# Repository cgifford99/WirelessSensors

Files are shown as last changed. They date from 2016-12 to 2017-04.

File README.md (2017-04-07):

# WirelessSensors
Wireless Sensors Flex Friday project repo

Here's a link to our Waffle.io management board: https://waffle.io/cgifford99/WirelessSensors/join

## Current Schedule
- [x] Project Proposal  | September 11th-September 30th
- [x] Research          | September 30th-October 7th
- [ ] Data pro design   | October 7th- December 23rd
- [ ] Testing/Debugging | December 23rd-April 7th 2017
- [ ] Finalize product  | March 3rd 2017-May 19th 2017
- [ ] Presentation      | May 19th 2017-June 9th 2017

# Wireless Sensors Proposal
## Abstract
The Wireless Sensor group’s overall goal is to create an easier and more cost-effective way to wirelessly transmit data from classroom   experiments from sensors through a communication chip to internet-enabled devices such as computers, laptops, tablets and smartphones. This system will allow students to easily customize how data is collected and manipulate data to fit their needs. It also allows teachers to view   the student’s data. Although this system will be useful in many fields, the project is going to initially focus on the educational market. This technology currently exists from other corporations, but it’s slow, expensive, complicated and unreliable. The team’s alternative will be faster, less expensive, user friendly and will deliver consistent results again and again. Furthermore, the current systems use wires, that get tangled and get lost. All of these wires can be eliminated with the use of radio communication and this is what the Wireless Sensor Team plans to do.

## Problem Statement
Currently there is no easy way to collect, store and share data from classroom science experiments simply by running the experiment and having data automatically appear on a shared website using low-cost components and inexpensive, yet effective software. Vernier is a company that produces a product along the lines of what we are creating, but it’s expensive, slow, and hard to access data. Products produced by Vernier, such as LabQuest, cost over $300 and need the use of another source, such as a PC, to process the collected data.

## Goals and Objectives
* Goal 1: Create a working prototype that sends information from a Raspberry Pi Zero/Arduino Micro to a Raspberry Pi 3.

  * Objective A: Discuss what teams are necessary, what project managing software to use, whether to use a Raspberry Pi Zero or an Arduino Micro to control the sensors and whether to make another prototype for the Rpi Zero or not.
  * Objective B: If the Rpi Zero is going to be used, code will need to be converted from the Arduino C++ language to C++ on the Rpi Zero.
  * Objective C: Create a prototype that includes the necessary components to interact with the Rpi 3 (the Hub).
  * Objective D: Debug data collection process and code (if necessary).

* Goal 2: Develop a cloud-based software for data storage and data transfer.

  * Objective A: Study Flask-SQLAlchemy (a framework to connect to a SQL database on the Rpi 3 and a browser on another device)
  * Objective B: Create and test a connection between the Rpi 3 SQL database and Flask-SQLAlchemy

* Goal 3: Finalize the product so that it both looks and works well for users.

  * Objective A: Design, order and solder a PCB (printed circuit board) that integrates with the Rpi Zero as well as the Rpi 3 in a more compact and visually attractive method.
  * Objective B: Use solidworks or another 3D design software to design an enclosure for the Rpi 3 and the Rpi Zero/Arduino Micro.
  * Objective C: Complete, debug and finish the product.
  
## Our Team
**Christopher Gifford**: Christopher is a Junior and project manager of the Wireless Sensors group. Last year he managed the sensors portion of the wireless group and learned a variety of other skills like 3D design, PCB design, and more C++ programming since then. 

**Lewis Woodard**: Lewis is a Sophomore at Baxter Academy for Technology and Science who is a part of the Wireless Sensors project for the second year. He hopes to focus his efforts in the project towards hardware and enclosures, which will include PCB design and using SolidWorks to design enclosures, cases, and other devices to contain sensors. Last year Lewis joined after completing the Pentathlon and worked on a combination of hardware, enclosures and software. Since last year, Lewis has gained more experience in C++ programming, CAD and more. Lewis plans to use this knowledge to focus mainly on hardware, pcb and 3D design, assisting on programming and software when he is needed.

**Connor Bell**: (NOTE: Connor is no longer involved with the project) Connor is a Junior at Baxter Academy for Technology and Science. He is a new addition to the Wireless Sensors project. He has taken multiple classes based around electronics and computer programming, and is currently learning as much as he can to have enough knowledge to be successful on this projects. Connor has programmed multiple web-based and non-web based programs in various languages such as Python and Javascript, both of which are relevant to the progress of this project.

**Curtis**: 
Curtis is a Sophomore at Baxter Academy for Technology and Science. He is also a new addition to the Wireless Sensors project. He has taken multiple classes based around electronics and computer programming. Curtis plans to concentrate on programming so that he be a productive member of the group.

**Ryan Cunningham**: Ryan is a freshman a Baxter. He is also a new addition to the Wireless Sensors project. He has lots of experience in HTML and CSS, he also is skilled in GUI design and graphics works. 

## Timeline
Currently unavailable

## Resources
* The school has tools like 3d printing software and equipment, soldering irons and other useful PCB design tools.
* Alan Lukas, Hal, Wells and Amory have backgrounds in programming, 3D design and PCB design and their knowledge will be very useful in the project.
* Currently an arduino prototype (Sensor prototype) and a Raspberry Pi 3 prototype (Hub prototype), are functioning from last year.    However, the Arduino did not have sufficient memory to hold a large number of different data acquisition formats.    The current plan is to use a RPi Zero instead for the Arduino for the sensor prototype.
* Purchase a  variety of Vernier sensors or borrow them as required from Baxter’s inventory.

## Constraints
* The team’s experience in PCB design, C++ programming, 3D design and other skill sets will influence how smoothly the project goes.
* There is not enough time this year to set-up a business and market the product to schools and other educational services.
* Accidents like damaging the circuits or short-circuiting them has been a problem in the past.
* There will be plenty of distractions and time constraints, but the team will use detailed schedules (Kanban and Gantter) to stay on track.

## Budget
Currently unavailable

## Deliverables
The final product will be a marketable platform to use in a classroom environment for experiments and laboratory tests in different subjects including physics, chemistry, and others. It will be made up of a Raspberry Pi Zeros (sensors) and a larger Raspberry Pi (hub). The hub will store and organize all data into a database and then send these data to a common cloud-based web server. Students can then connect to this web site to compare results of the data collected in the various class experiments. Note that data can also be collected from field experiments and then sent up to the cloud based server once the sensors connect to the RPi hub.

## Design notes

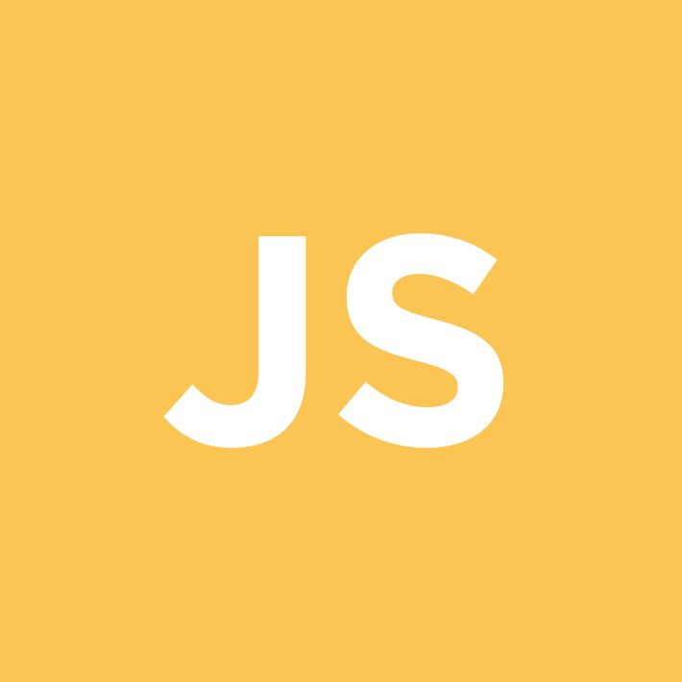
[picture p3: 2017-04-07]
server/client/images/user.jpg

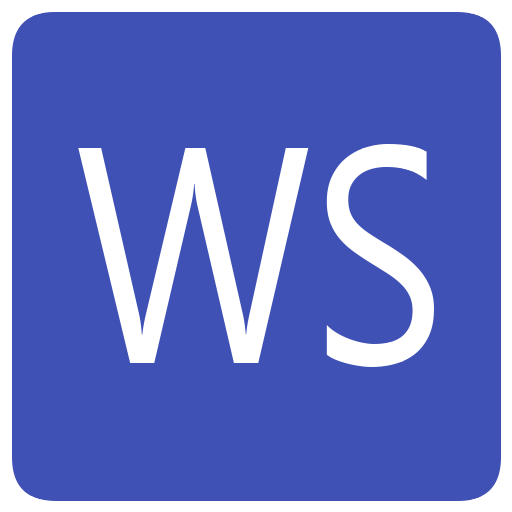
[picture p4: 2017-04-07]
server/client/images/android-desktop.png

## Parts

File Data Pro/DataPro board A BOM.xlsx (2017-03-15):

Part Name | Value | Device | Package | Description | Retailer | Retailer Part # | Manufacturer Part # | Quantity
B1 | CR2032 | CR2032SMT | CR2032-SMD |  | Digikey | BRX1-2032-SMCT-ND | BRX1-2032-SM | 1
C1 | 0.1uFd | C-USC0805 | C0805 | CAPACITOR, American symbol | Digikey | 311-1142-1-ND | CC0805KRX7R7BB104 | 2
D1 |  | DIODESOD-323F | SOD-323F | Diode | Digikey | MM3Z3V3BTR-ND | MM3Z3V3B | 1
D3 |  | DIODESMB | SMB-DIODE | Diode | Digikey | 1SMB5928BT3GOSCT-ND | 1SMB5928BT3G | 1
IC1 | 4049N | 4049N | DIL16 | Hex inverting BUFFER | Digikey | 296-29273-1-ND | CD74HC4049NSR | 1
IC2 | MCP3008 | MCP3008 | DIL16 |  | Digikey | MCP3008-I/P-ND | MCP3008-I/P | 1
IC3, IC7 | LM324D | LM324D | SO14 | OP AMP | Digikey | 497-1580-1-ND | LM324DT | 2
J1 | RASPBERRYPI-40-PIN-GPIO | RASPBERRYPI-40-PIN-GPIO | 2X20-SHROUDED | Raspberry Pi GPIO Header | Digikey | 1528-1785-ND | 2222 | 1
J2-J5 | A2 | M06VERNIER-ANALOG | BTA | Header 6 | https://www.sparkfun.com/products/12753 |  |  | 4
J6-J9 | D1 | M06VERNIER-DIGITAL | BTD | Header 6 | https://www.sparkfun.com/products/12754 |  |  | 4
JP2 |  | PINHD-1X4 | 1X04 | PIN HEADER
JP3 |  | PINHD-1X2 | 1X02 | PIN HEADER
JP4 |  | PINHD-1X5 | 1X05 | PIN HEADER
LED1 |  | LEDCHIP-LED0805 | CHIP-LED0805 | LED | Digikey | 475-1278-1-ND | LS R976-NR-1 | 1
R1-R8, R10, R17-R26 | 1k | R-US_R0805 | R0805 | RESISTOR, American symbol | Digikey | 311-1.0KARCT-ND | RC0805JR-071KL | 17
R9 | 4.7k | R-US_R0805 | R0805 | RESISTOR, American symbol | Digikey | 311-4.70KCRCT-ND | RC0805FR-074K7L | 1
R11, R15, R16 | 3.3k | R-US_R0805 | R0805 | RESISTOR, American symbol | Digikey | 311-3.3KARCT-ND | RC0805JR-073K3L | 3
R12 | 200 | R-US_R0805 | R0805 | RESISTOR, American symbol | Digikey | 311-200CRTR-ND | RC0805FR-07200RL | 1
R13 | 1.5M | R-US_R0805 | R0805 | RESISTOR, American symbol | Digikey | 311-1.5MARTR-ND | RC0805JR-071M5L | 1
R14 | 510K | R-US_R0805 | R0805 | RESISTOR, American symbol | Digikey | 311-510KARCT-ND | RC0805JR-07510KL | 1
U$2 | DS1307SO8-TIGHT | DS1307SO8-TIGHT | SO08-TIGHT | I2C real-time clock with battery backup. | Digikey | DS1307Z+T&RCT-ND | DS1307Z+T&R | 1
U1 | DS18B20 | DS18B20 | TO-92-AMMO | DS18B20 1-wire temperature sensor | Digikey | DS18B20+-ND | DS18B20+ | 1
X1 | 32.768khz | CRYSTALTC38H | TC38H | CRYSTAL | Digikey | 535-9034-ND | AB38T-32.768KHZ | 1

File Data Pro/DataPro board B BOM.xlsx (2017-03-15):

Part Name | Value | Device | Package | Description | Retailer | Retailer Part # | Manufacturer Part # | Quantity
BATT1 |  | JST_2PIN-SMT-RA | JST-PH-2-SMT-RA | JST 2-Pin Connectors of various flavors | Digikey | 455-1734-2-ND | B2B-PH-SM4-TB(LF)(SN) | 1
C1 | 2.2uF | C-USC0805 | C0805 | CAPACITOR, American symbol | Digikey | 587-1293-1-ND | EMK212BJ225KG-T | 1
C2 | 2.2uF | C-USC1206 | C1206 | CAPACITOR, American symbol | Digikey | 399-8180-1-ND | C1206C225K3RACTU | 1
C3 | 1uF | C-USC1206 | C1206 | CAPACITOR, American symbol | Digikey | 399-1254-1-ND | C1206C105K4RACTU | 1
C4 | 1uF | C-USC1206 | C1206 | CAPACITOR, American symbol | Digikey | 399-1254-1-ND | C1206C105K4RACTU | 1
C5 | 2.2uF | C-USC1206 | C1206 | CAPACITOR, American symbol | Digikey | 399-8180-1-ND | C1206C225K3RACTU | 1
C11 | 22uF | CAP0805 | C0805 | CAPACITOR, American symbol | Digikey | 490-10747-1-ND | GRM21BR61C226ME44L | 1
C12 | 0.1uF | CAP0603-CAP | 0603-CAP | CAPACITOR, American symbol | Digikey | 311-1088-1-ND | CC0603KRX7R7BB104 | 1
C13 | 0.1uF | CAP0603-CAP | 0603-CAP | CAPACITOR, American symbol | Digikey | 311-1088-1-ND | CC0603KRX7R7BB104 | 1
C14 | 10uF | CAP1206 | C1206 | CAPACITOR, American symbol | Digikey | 311-1376-1-ND | CC1206ZKY5V7BB106 | 1
C15 | 10uF | C-USC0805K | C0805K | CAPACITOR, American symbol | Digikey | 399-8012-1-ND | C0805C106K4PACTU | 1
C16 | 10uF | C-USC0805K | C0805K | CAPACITOR, American symbol | Digikey | 399-8012-1-ND | C0805C106K4PACTU | 1
C17 | 10uF | C-USC0805K | C0805K | CAPACITOR, American symbol | Digikey | 399-8012-1-ND | C0805C106K4PACTU | 1
C18 | 4700uF/10V | CPOL-USE5-13 | E5-13 | POLARIZED CAPACITOR, American symbol | Digikey | 493-1028-ND | UVR1A472MHD | 1
CHRG/LBO1 | ORANGE | LED0805_NOOUTLINE | CHIPLED_0805_NOOUTLINE | LED | Digikey | 160-1413-1-ND | LTST-C170KFKT | 1
CN2 | DCIN | DCBARRELSMT | DCJACK_2MM_SMT | DC Barrel Jack | Digikey | CP-002AHPJCT-ND | PJ-002AH-SMT-TR | 1
D1 | MBR0520LT | MBR0520LT | SOD123 | SCHOTTKY BARRIER RECTIFIER | Digikey | MBR0520LT1GOSTR-ND | MBR0520LT1G | 1
D2 | MBR0520LT | MBR0520LT | SOD123 | SCHOTTKY BARRIER RECTIFIER | Digikey | MBR0520LT1GOSTR-ND | MBR0520LT1G | 1
D3 | MBR0520LT | MBR0520LT | SOD123 | SCHOTTKY BARRIER RECTIFIER | Digikey | MBR0520LT1GOSTR-ND | MBR0520LT1G | 1
D4 | MBR120VLSFT1G | DIODESOD-123 | SOD-123 | Diode | Digikey | MBR120VLSFT1GOSTR-ND | MBR120VLSFT1G | 1
D5 | MBR0520LT | MBR0520LT | SOD123 | SCHOTTKY BARRIER RECTIFIER | Digikey | MBR0520LT1GOSTR-ND | MBR0520LT1G | 1
DONE1 | GREEN | LED0805_NOOUTLINE | CHIPLED_0805_NOOUTLINE | LED | Digikey | 475-1410-1-ND | LG R971-KN-1 | 1
IC8 | MCP73871 | MCP73871 | QFN20_4MM |  | Digikey | MCP73871-2AAI/ML-ND | MCP73871-2AAI/ML | 1
JP1 |  | PINHD-1X5 | 1X05 | PIN HEADER
JP2 | ESP8266 | PINHD-2X4 | 2X04 | PIN HEADER
JP3 |  | PINHD-1X4 | 1X04 | PIN HEADER
JP4 |  | PINHD-1X2 | 1X02 | PIN HEADER
L1 | 3.3uH | CR43 | CR43 | Power Inductor | Digikey | 308-1525-1-ND | CR43NP-3R3MC | 1
L2 | 4.7uH, 1.2A | INDUCTOR. | L3225M | Inductors | Digikey | 587-2166-1-ND | BRL3225T4R7M | 1
M1 | WIRELESS-NRF24L01 | WIRELESS-NRF24L01 | WIRELESS-NRF24L01 | 2.4 GHz Wireless Module based on NRF24L01 chip
PWR1 | RED | LED0805_NOOUTLINE | CHIPLED_0805_NOOUTLINE | LED | Digikey | 475-1415-2-ND | LH R974-LP-1 | 1
R1 | 13.3k | R-US_R0805 | R0805 | RESISTOR, American symbol | Digikey | 311-13.3KCRTR-ND | RC0805FR-0713K3L | 1
R2 | 147k | R-US_R0805 | R0805 | RESISTOR, American symbol | Digikey | 311-147KCRTR-ND | RC0805FR-07147KL | 1
R39 | 2M | RESISTOR0603-RES | 0603-RES | Resistor | Digikey | 311-2.0MGRTR-ND | RC0603JR-072ML | 1
R40 | 220k | RESISTOR0603-RES | 0603-RES | Resistor | Digikey | 311-220KJRTR-ND | RC0402JR-07220KL | 1
R41 | 1.2M | RESISTOR0603-RES | 0603-RES | Resistor | Digikey | 311-1.2MGRTR-ND | RC0603JR-071M2L | 1
R42 | 220k | RESISTOR0603-RES | 0603-RES | Resistor | Digikey | 311-220KJRTR-ND | RC0402JR-07220KL | 1
R43 | 2M | RESISTOR0603-RES | 0603-RES | Resistor | Digikey | 311-2.0MGRTR-ND | RC0603JR-072ML | 1
R44 | 270K | R-US_R0805 | R0805 | RESISTOR, American symbol | Digikey | 311-270KARTR-ND | RC0805JR-07270KL | 1
R45 | 100K | R-US_R0805 | R0805 | RESISTOR, American symbol | Digikey | 311-100KCRTR-ND | RC0805FR-07100KL | 1
R46 | 1K | R-US_R0805 | R0805 | RESISTOR, American symbol | Digikey | 311-1.0KARTR-ND | RC0805JR-071KL | 1
R47 | 1K | R-US_R0805 | R0805 | RESISTOR, American symbol | Digikey | 311-1.0KARTR-ND | RC0805JR-071KL | 1
R48 | 1K | R-US_R0805 | R0805 | RESISTOR, American symbol | Digikey | 311-1.0KARTR-ND | RC0805JR-071KL | 1
R49 | 2K | R-US_FLIPFLOP | 0805-THM | RESISTOR, American symbol |  |  |  | 1
R50 | 100K | R-US_R0805 | R0805 | RESISTOR, American symbol | Digikey | 311-100KCRTR-ND | RC0805FR-07100KL | 1
R51 | 1K | R-US_M0805 | M0805 | RESISTOR, American symbol | Digikey | 311-1.0KARTR-ND | RC0805JR-071KL | 1
RT1 | 150K | R-US_M0805 | M0805 | RESISTOR, American symbol | Digikey | 311-150KARTR-ND | RC0805JR-07150KL | 1
THERM1 | 10K | R-US_FLIPFLOP | 0805-THM | RESISTOR, American symbol
U$3 | V_REG_LD1117VXX | V_REG_LD1117VXX | 78XXL | LD1117VXX voltage regulator. We carry the 3.3V version (COM-00526) in TO-220 package. | Sparkfun | https://www.sparkfun.com/products/526 | https://www.sparkfun.com/products/526
U1 | LT1930AES5PBF | LT1930AES5PBF | SOT95P280X145-5N | DC/DC Converter | Digikey | LT1930AES5#TRMPBFTR-ND | LT1930AES5#TRMPBF | 1
U3 | TPS61200 | TPS61200 | QFN-10_PAD | DC to DC Booster | Digikey | 296-27017-1-ND | TPS61200DRCR | 1

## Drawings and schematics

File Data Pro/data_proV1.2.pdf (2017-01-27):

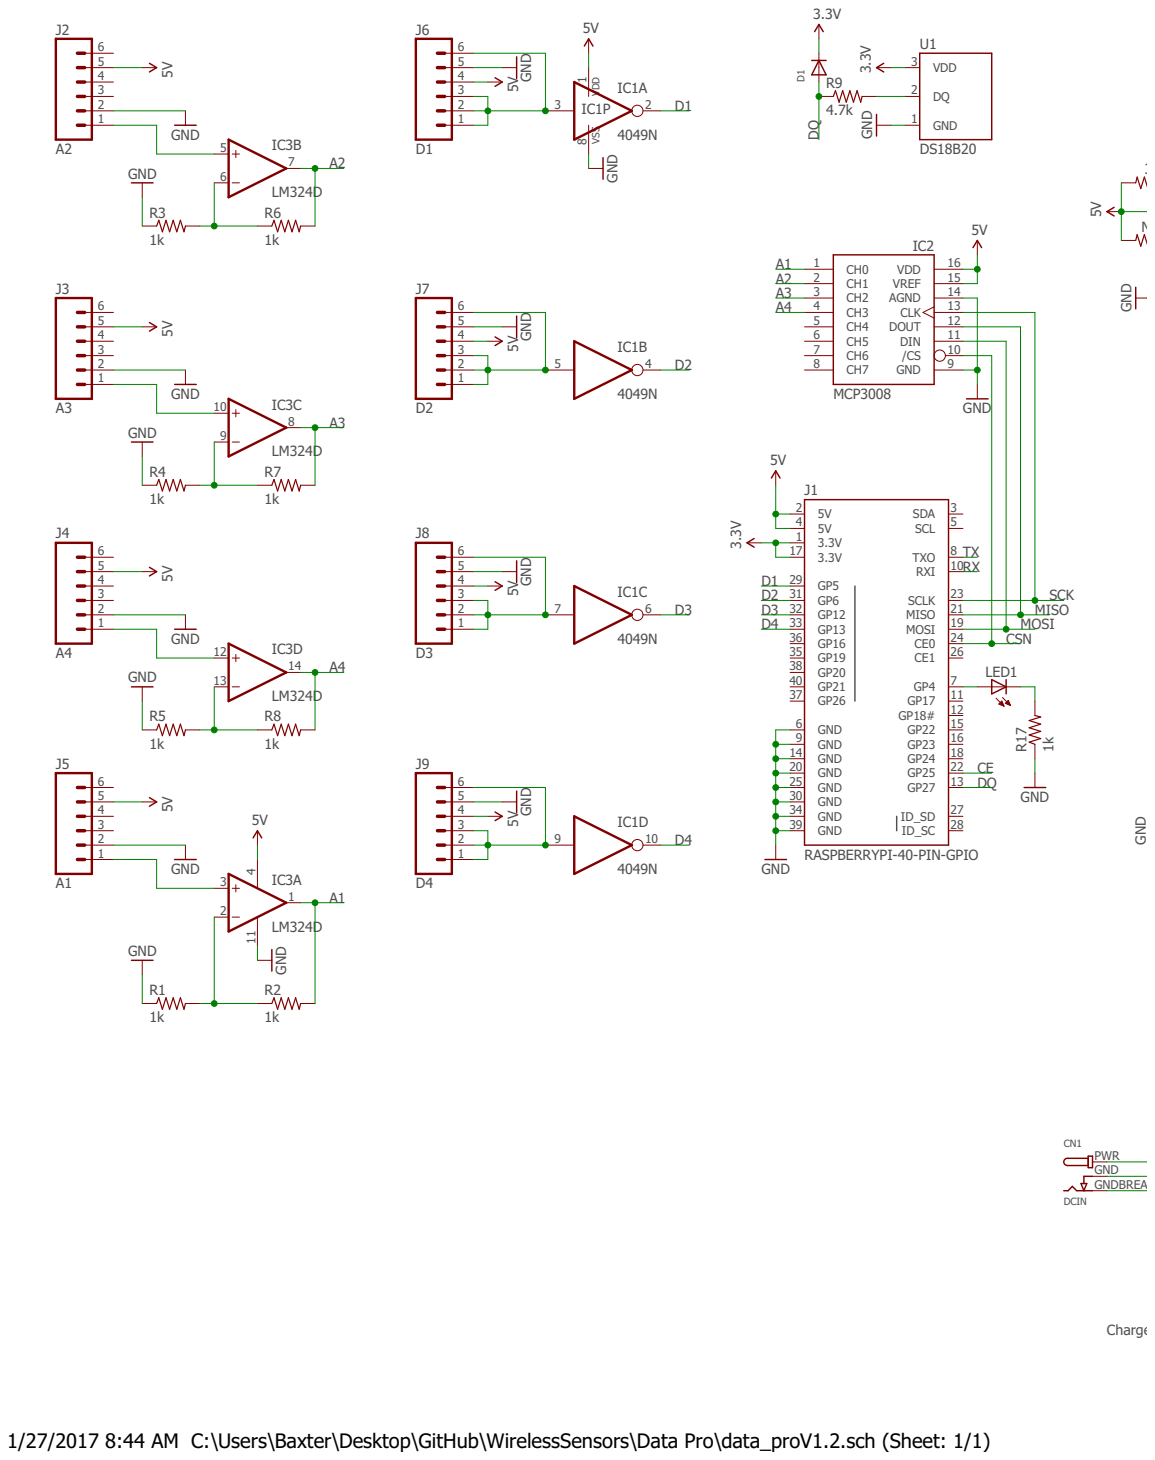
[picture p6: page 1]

1/27/2017 8:44 AM C:\Users\Baxter\Desktop\GitHub\WirelessSensors\Data Pro\data_proV1.2.sch (Sheet: 1/1)

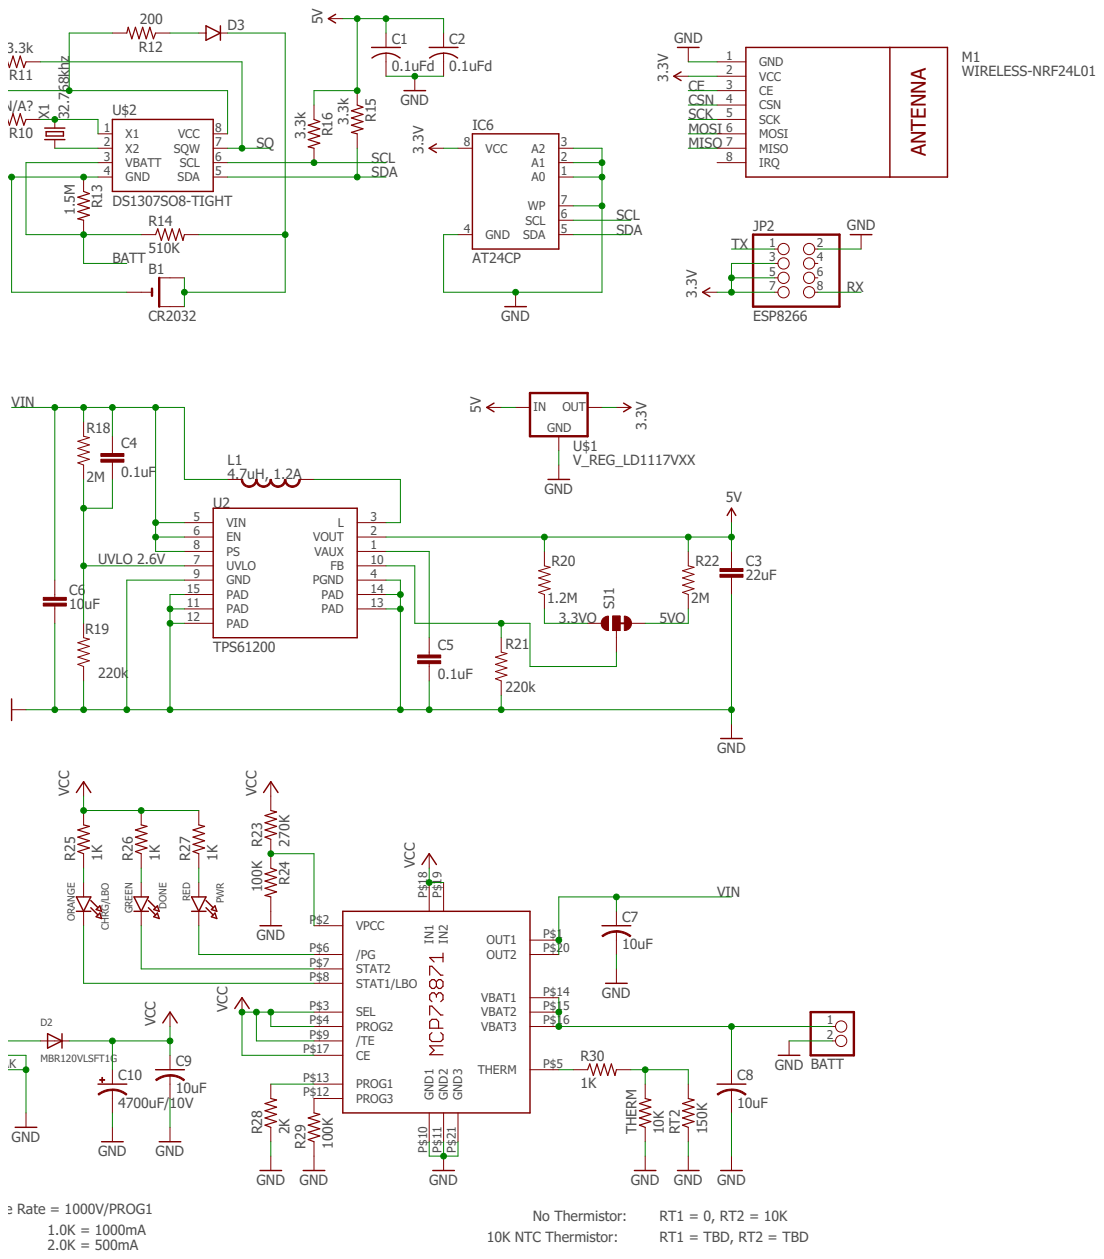
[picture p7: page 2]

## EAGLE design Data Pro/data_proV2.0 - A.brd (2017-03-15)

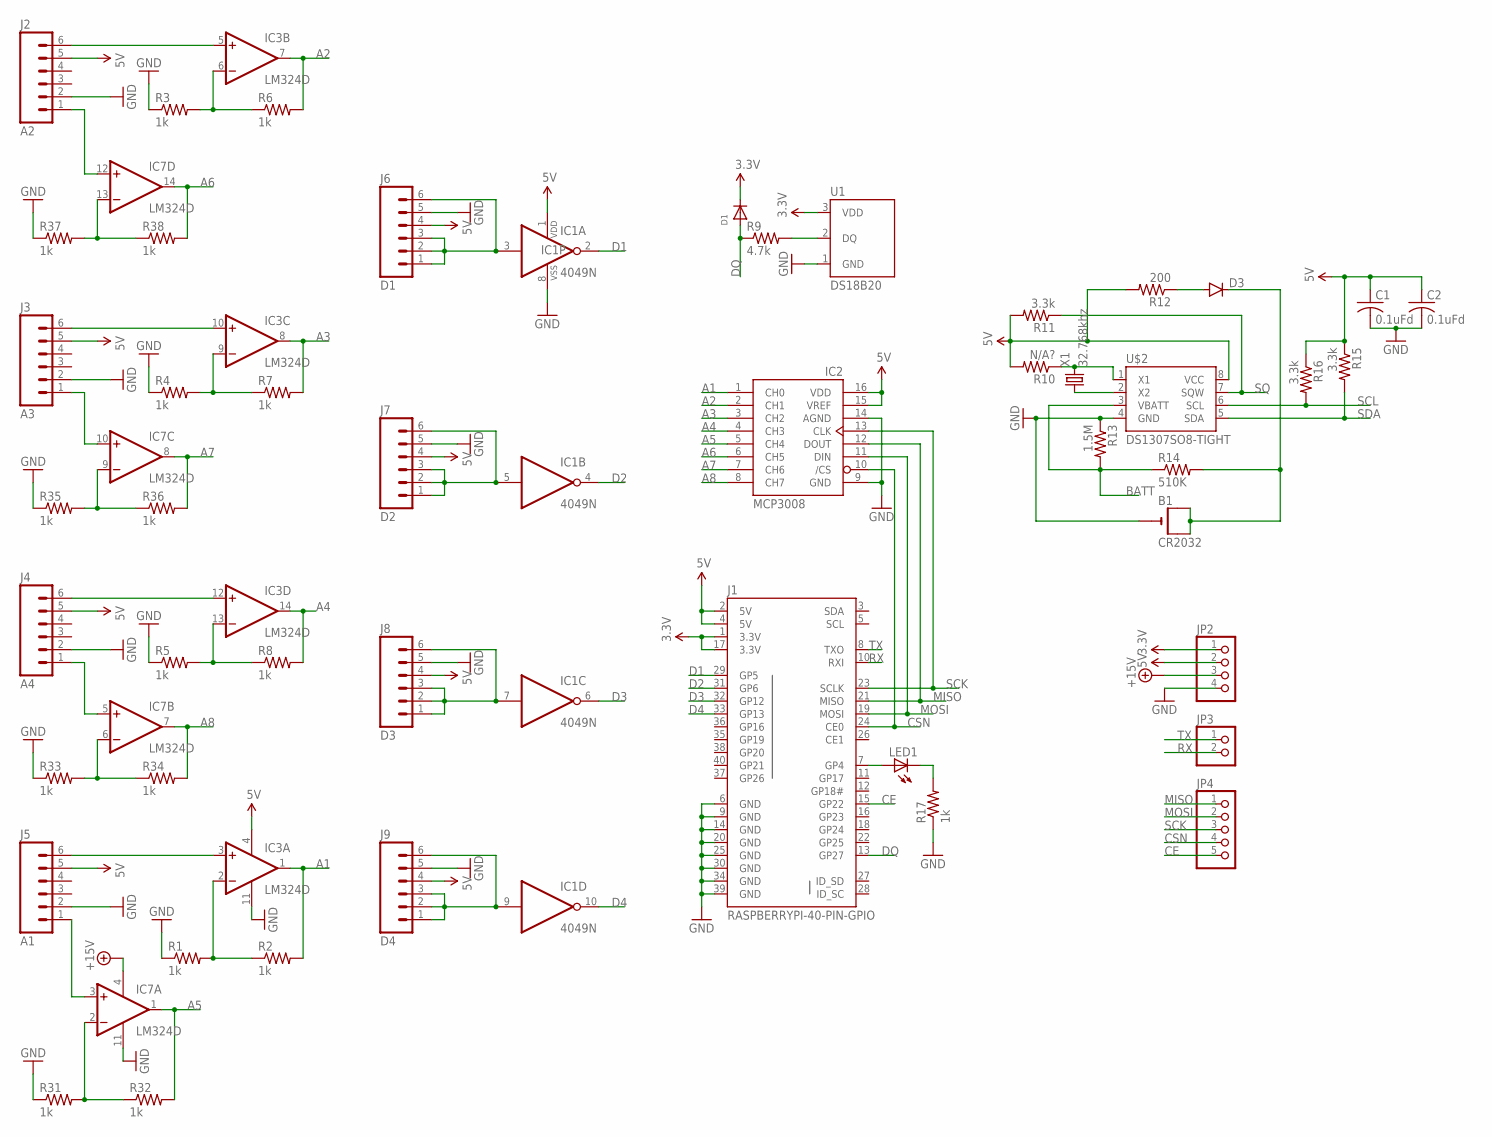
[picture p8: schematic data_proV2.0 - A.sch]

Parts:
B1: CR2032; CR2032-SMD
C1, C2: 0.1uFd; C0805
D1: DIODESOD-323F; SOD-323F
D3: DIODESMB; SMB-DIODE
IC1: 4049N; DIL16
IC2: MCP3008; DIL16
IC3, IC7: LM324D; SO14
J1: RASPBERRYPI-40-PIN-GPIO; 2X20-SHROUDED
J2: A2; BTA
J3: A3; BTA
J4: A4; BTA
J5: A1; BTA
J6: D1; BTD
J7: D2; BTD
J8: D3; BTD
J9: D4; BTD
JP2: PINHD-1X4; 1X04
JP3: PINHD-1X2; 1X02
JP4: PINHD-1X5; 1X05
LED1: LEDCHIP-LED0805; CHIP-LED0805
R1, R2, R3, R4, R5, R6, R7, R8, R17, R31, R32, R33, R34, R35, R36, R37, R38: 1k; R0805
R9: 4.7k; R0805
R10: N/A?; R0805
R11, R15, R16: 3.3k; R0805
R12: 200; R0805
R13: 1.5M; R0805
R14: 510K; R0805
U1: DS18B20; TO-92-AMMO
U$2: DS1307SO8-TIGHT; SO08-TIGHT
X1: 32.768khz; TC38H

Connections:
3.3V: D1.C, J1.1 (3.3V), J1.17 (3.3V), JP2.1, U1.3 (VDD)
5V: C1.1, C2.1, IC1.1 (VDD), IC2.15 (VREF), IC2.16 (VDD), IC3.4 (V+), J1.2 (5V), J1.4 (5V), J2.5, J3.5, J4.5, J5.5, J6.4, J7.4, J8.4, J9.4, JP2.2, R10.2, R11.2, R12.2, R15.1, R16.1, U$2.8 (VCC)
+15V: IC7.4 (V+), JP2.3
A1: IC2.1 (CH0), IC3.1 (OUT), R2.2
A2: IC2.2 (CH1), IC3.7 (OUT), R6.2
A3: IC2.3 (CH2), IC3.8 (OUT), R7.2
A4: IC2.4 (CH3), IC3.14 (OUT), R8.2
A5: IC2.5 (CH4), IC7.1 (OUT), R32.2
A6: IC2.6 (CH5), IC7.14 (OUT), R38.2
A7: IC2.7 (CH6), IC7.8 (OUT), R36.2
A8: IC2.8 (CH7), IC7.7 (OUT), R34.2
BATT: R13.2, R14.1, U$2.3 (VBATT)
CE: J1.15 (GP22), JP4.5
CSN: IC2.10 (/CS), J1.24 (CE0), JP4.4
D1: IC1.2 (O), J1.29 (GP5)
D2: IC1.4 (O), J1.31 (GP6)
D3: IC1.6 (O), J1.32 (GP12)
D4: IC1.10 (O), J1.33 (GP13)
DQ: D1.A, J1.13 (GP27), R9.1
GND: B1.-, C1.2, C2.2, IC1.8 (VSS), IC2.9 (GND), IC2.14 (AGND), IC3.11 (V-), IC7.11 (V-), J1.6 (GND), J1.9 (GND), J1.14 (GND), J1.20 (GND), J1.25 (GND), J1.30 (GND), J1.34 (GND), J1.39 (GND), J2.2, J3.2, J4.2, J5.2, J6.5, J7.5, J8.5, J9.5, JP2.4, R1.1, R3.1, R4.1, R5.1, R13.1, R17.1, R31.1, R33.1, R35.1, R37.1, U1.1 (GND), U$2.4 (GND)
MISO: IC2.12 (DOUT), J1.21 (MISO), JP4.1
MOSI: IC2.11 (DIN), J1.19 (MOSI), JP4.2
unnamed: U$2.2 (X2), X1.1
unnamed: R10.1, U$2.1 (X1), X1.2
unnamed: B1.+$1 (+), B1.+$2 (+1), D3.C, R14.2
unnamed: J1.7 (GP4), LED1.A
unnamed: IC3.2 (-IN), R1.2, R2.1
unnamed: R9.2, U1.2 (DQ)
unnamed: IC3.13 (-IN), R5.2, R8.1
unnamed: IC3.6 (-IN), R3.2, R6.1
unnamed: D3.A, R12.1
unnamed: IC1.3 (I), J6.1, J6.2, J6.3, J6.6
unnamed: IC1.5 (I), J7.1, J7.2, J7.3, J7.6
unnamed: IC1.7 (I), J8.1, J8.2, J8.3, J8.6
unnamed: IC1.9 (I), J9.1, J9.2, J9.3, J9.6
unnamed: IC3.9 (-IN), R4.2, R7.1
unnamed: LED1.C, R17.2
unnamed: IC3.3 (+IN), J5.6
unnamed: IC7.2 (-IN), R31.2, R32.1
unnamed: IC7.3 (+IN), J5.1
unnamed: IC7.6 (-IN), R33.2, R34.1
unnamed: IC7.9 (-IN), R35.2, R36.1
unnamed: IC7.13 (-IN), R37.2, R38.1
unnamed: IC7.12 (+IN), J2.1
RX: J1.10 (RXI), JP3.2
S1-5V1: IC3.5 (+IN), J2.6
S1-5V2: IC3.10 (+IN), J3.6
S1-5V3: IC7.5 (+IN), J4.1
S1-5V4: IC3.12 (+IN), J4.6
S1-5V5: IC7.10 (+IN), J3.1
SCK: IC2.13 (CLK), J1.23 (SCLK), JP4.3
SCL: R16.2, U$2.6 (SCL)
SDA: R15.2, U$2.5 (SDA)
SQ: R11.1, U$2.7 (SQW)
TX: J1.8 (TXO), JP3.1

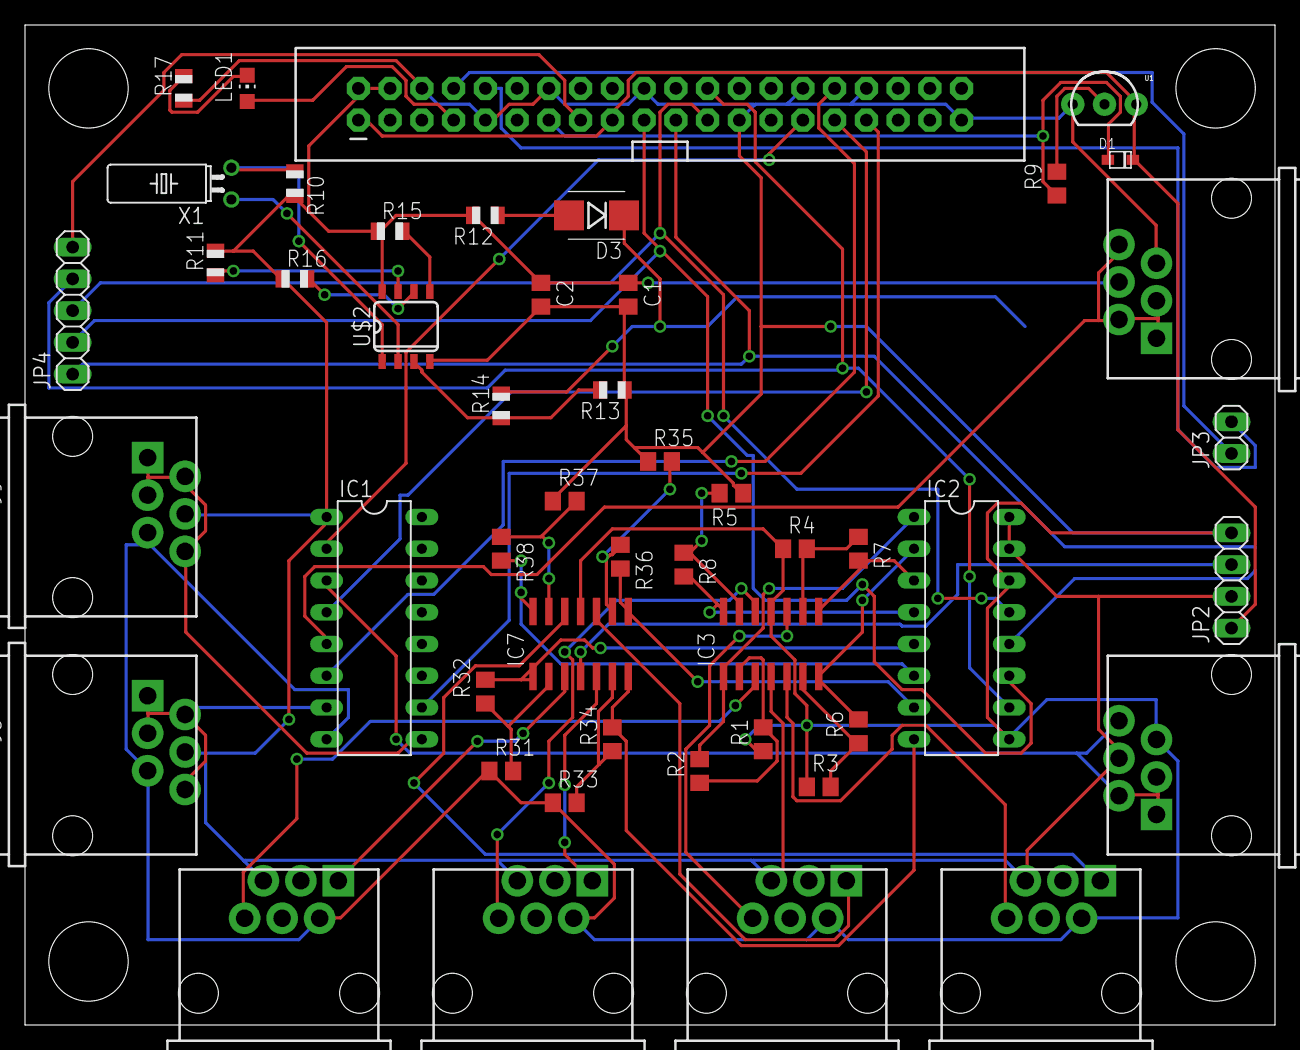
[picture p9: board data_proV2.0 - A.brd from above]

Board: 2 copper layers, 100.0 x 80.0 mm, 50 parts (1 on the bottom side), 55 nets.

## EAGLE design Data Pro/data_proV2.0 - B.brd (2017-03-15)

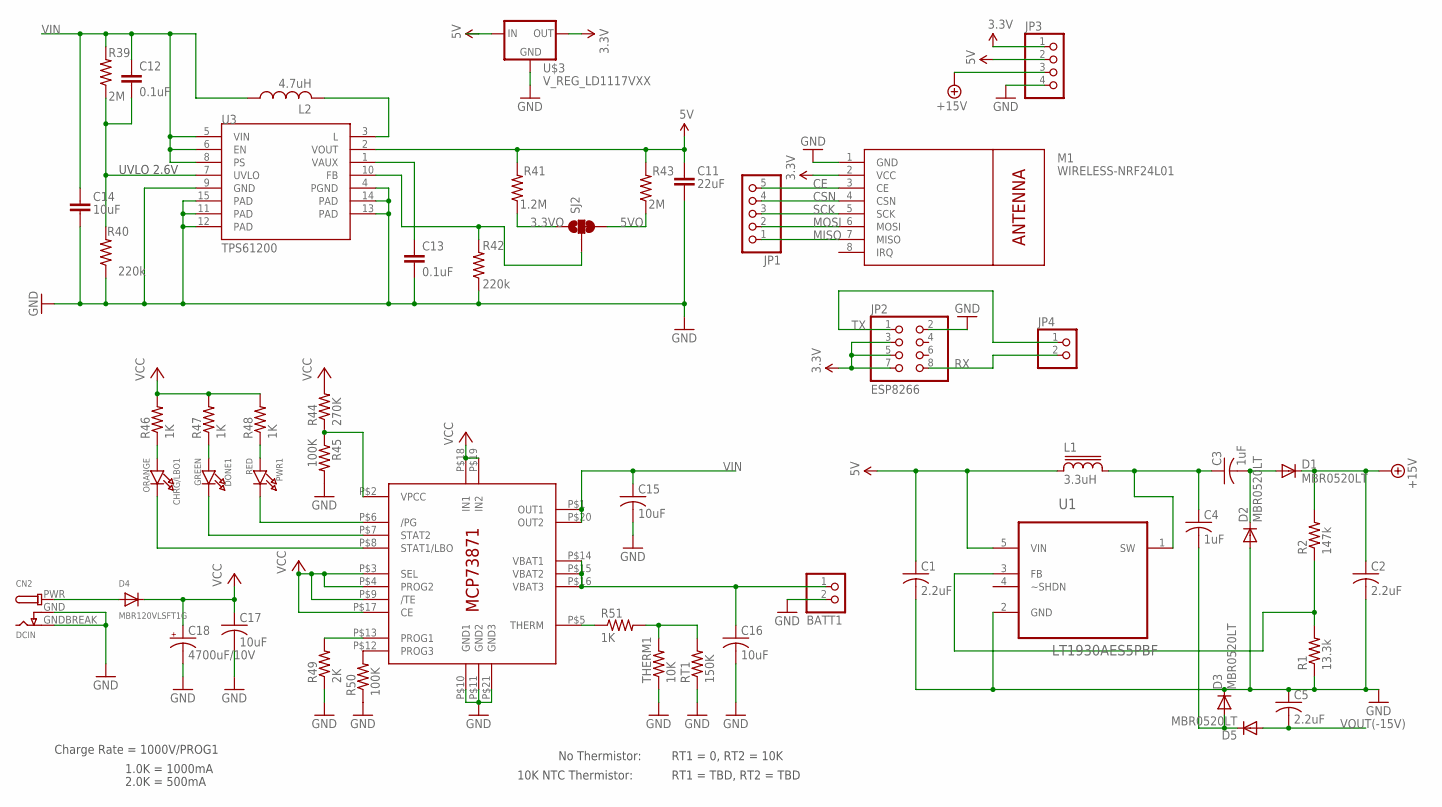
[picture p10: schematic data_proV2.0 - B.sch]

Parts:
BATT1: JST_2PIN-SMT-RA; JST-PH-2-SMT-RA
C1: 2.2uF; C0805
C2, C5: 2.2uF; C1206
C3, C4: 1uF; C1206
C11: 22uF; 0805
C12, C13: 0.1uF; 0603-CAP
C14: 10uF; 1206
C15, C16, C17: 10uF; C0805K
C18: 4700uF/10V; E5-13
CHRG/LBO1: ORANGE; CHIPLED_0805_NOOUTLINE
CN2: DCIN; DCJACK_2MM_SMT
D1, D2, D3, D5: MBR0520LT; SOD123
D4: MBR120VLSFT1G; SOD-123
DONE1: GREEN; CHIPLED_0805_NOOUTLINE
IC8: MCP73871; QFN20_4MM
JP1: PINHD-1X5; 1X05
JP2: ESP8266; 2X04
JP3: PINHD-1X4; 1X04
JP4: PINHD-1X2; 1X02
L1: 3.3uH; CR43
L2: 4.7uH; L3225M
M1: WIRELESS-NRF24L01
PWR1: RED; CHIPLED_0805_NOOUTLINE
R1: 13.3k; R0805
R2: 147k; R0805
R39, R43: 2M; 0603-RES
R40, R42: 220k; 0603-RES
R41: 1.2M; 0603-RES
R44: 270K; R0805
R45, R50: 100K; R0805
R46, R47, R48: 1K; R0805
R49: 2K; 0805-THM
R51: 1K; M0805
RT1: 150K; M0805
SJ2: SOLDERJUMPER_2WAYPASTE2&3; SJ_3_PASTE2&3
THERM1: 10K; 0805-THM
U1: LT1930AES5PBF; SOT95P280X145-5N
U3: TPS61200; QFN-10_PAD
U$3: V_REG_LD1117VXX; 78XXL

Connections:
3.3V: JP2.3, JP2.5, JP2.7, JP3.1, M1.2 (VCC), U$3.GND (OUT)
3.3VO: R41.1, SJ2.1
5V: C1.1, C11.1, JP3.2, L1.1, R41.2, R43.2, U1.5 (VIN), U3.2 (VOUT), U$3.OUT (IN)
5VO: R43.1, SJ2.3
+15V: C2.1, D1.C, JP3.3, R2.2
BATT2: BATT1.1 (2), C16.1, IC8.P$14 (VBAT1), IC8.P$15 (VBAT2), IC8.P$16 (VBAT3)
CE: JP1.5, M1.3 (CE)
CSN: JP1.4, M1.4 (CSN)
FB1: R42.2, SJ2.2, U3.10 (FB)
GND: BATT1.2 (1), C1.2, C2.2, C5.1, C11.2, C13.2, C14.2, C15.2, C16.2, C17.2, C18.-, CN2.GND (GNDBREAK), CN2.GNDBREAK (GND), D2.A, D3.C, IC8.P$10 (GND1), IC8.P$11 (GND2), IC8.P$21 (GND3), JP2.2, JP3.4, M1.1 (GND), R1.1, R40.1, R42.1, R45.2, R49.1, R50.1, RT1.1, THERM1.1, U1.2 (GND), U3.4 (PGND), U3.9 (GND), U3.11 (PAD), U3.12 (PAD), U3.13 (PAD), U3.14 (PAD), U3.15 (PAD), U$3.IN (GND)
MISO: JP1.1, M1.7 (MISO)
MOSI: JP1.2, M1.6 (MOSI)
unnamed: C4.2, D3.A, D5.C
unnamed: C3.1, C4.1, L1.2, U1.1 (SW)
unnamed: R1.2, R2.1, U1.3 (FB)
unnamed: C3.2, D1.A, D2.C
unnamed: L2.2, U3.3 (L)
unnamed: C13.1, U3.1 (VAUX)
unnamed: IC8.P$2 (VPCC), R44.1, R45.1
unnamed: IC8.P$6 (/PG), PWR1.C
unnamed: DONE1.C, IC8.P$7 (STAT2)
unnamed: CHRG/LBO1.C, IC8.P$8 (STAT1/LBO)
unnamed: CHRG/LBO1.A, R46.1
unnamed: DONE1.A, R47.1
unnamed: PWR1.A, R48.1
unnamed: IC8.P$12 (PROG3), R50.2
unnamed: IC8.P$13 (PROG1), R49.2
unnamed: IC8.P$5 (THERM), R51.1
unnamed: R51.2, RT1.2, THERM1.2
unnamed: CN2.PWR, D4.A
RX: JP2.8, JP4.2
SCK: JP1.3, M1.5 (SCK)
TX: JP2.1, JP4.1
UVLO1: C12.2, R39.1, R40.2, U3.7 (UVLO)
VCC: C17.1, C18.+, D4.C, IC8.P$3 (SEL), IC8.P$4 (PROG2), IC8.P$9 (/TE), IC8.P$17 (CE), IC8.P$18 (IN1), IC8.P$19 (IN2), R44.2, R46.2, R47.2, R48.2
VIN: C12.1, C14.1, C15.1, IC8.P$1 (OUT1), IC8.P$20 (OUT2), L2.1, R39.2, U3.5 (VIN), U3.6 (EN), U3.8 (PS)
VOUT(-15V): C5.2, D5.A

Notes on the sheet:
UVLO 2.6V
Charge Rate = 1000V/PROG1
1.0K = 1000mA
2.0K = 500mA
No Thermistor:
10K NTC Thermistor:
RT1 = 0, RT2 = 10K
RT1 = TBD, RT2 = TBD

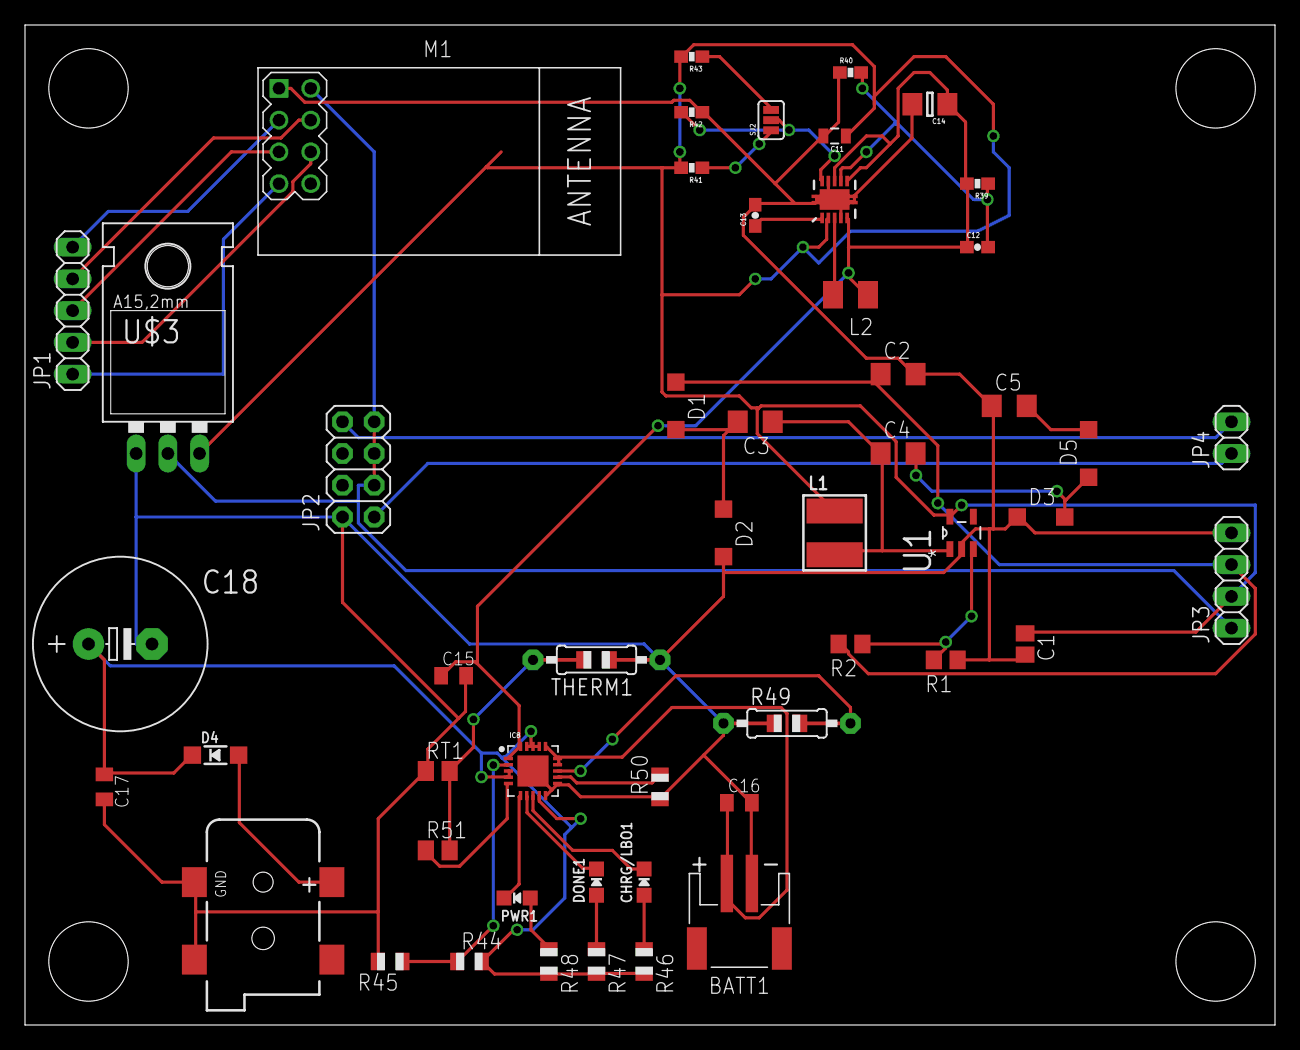
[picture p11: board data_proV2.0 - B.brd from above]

Board: 2 copper layers, 100.0 x 80.0 mm, 52 parts (0 on the bottom side), 37 nets.

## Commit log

2016-11-13 Data Pro Schematic (Unfinished)
    [data_pro.sch, data_proV1.sch, data_proV2.sch]
2016-11-28 Data pro schematic 11/28/16
    [data_proV2.brd, data_proV2.sch]
2016-12-09 Data pro update and Lewis' python code
    [data_pro.sch, data_proV1.sch, data_proV2.brd, data_proV2.sch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]
2017-01-10 Data pro update v1.2
    The schematic is complete, working on the board.
    [data_proV1.1.brd, data_proV1.1.sch, data_proV1.2.brd, data_proV1.2.sch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]
2017-01-19 Data pro update v1.2 (Complete)
    [data_proV1.2.brd, wireless_attachment.sch]
2017-01-20 Data pro complete
    [data_proV1.2.brd, data_proV1.2.sch]
2017-01-27 More data pro updates
    Sorry
    [data_proV1.2.brd, data_proV1.2.sch]
2017-03-15 First prototype complete
    [DataPro board A BOM.xlsx, DataPro board B BOM.xlsx, data_proV1.3.brd, data_proV1.3.sch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]

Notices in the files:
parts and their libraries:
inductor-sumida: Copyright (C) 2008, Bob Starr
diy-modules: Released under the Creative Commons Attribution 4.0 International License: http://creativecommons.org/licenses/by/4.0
